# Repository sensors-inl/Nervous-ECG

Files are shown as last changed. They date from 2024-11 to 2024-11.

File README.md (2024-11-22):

<p align="center">
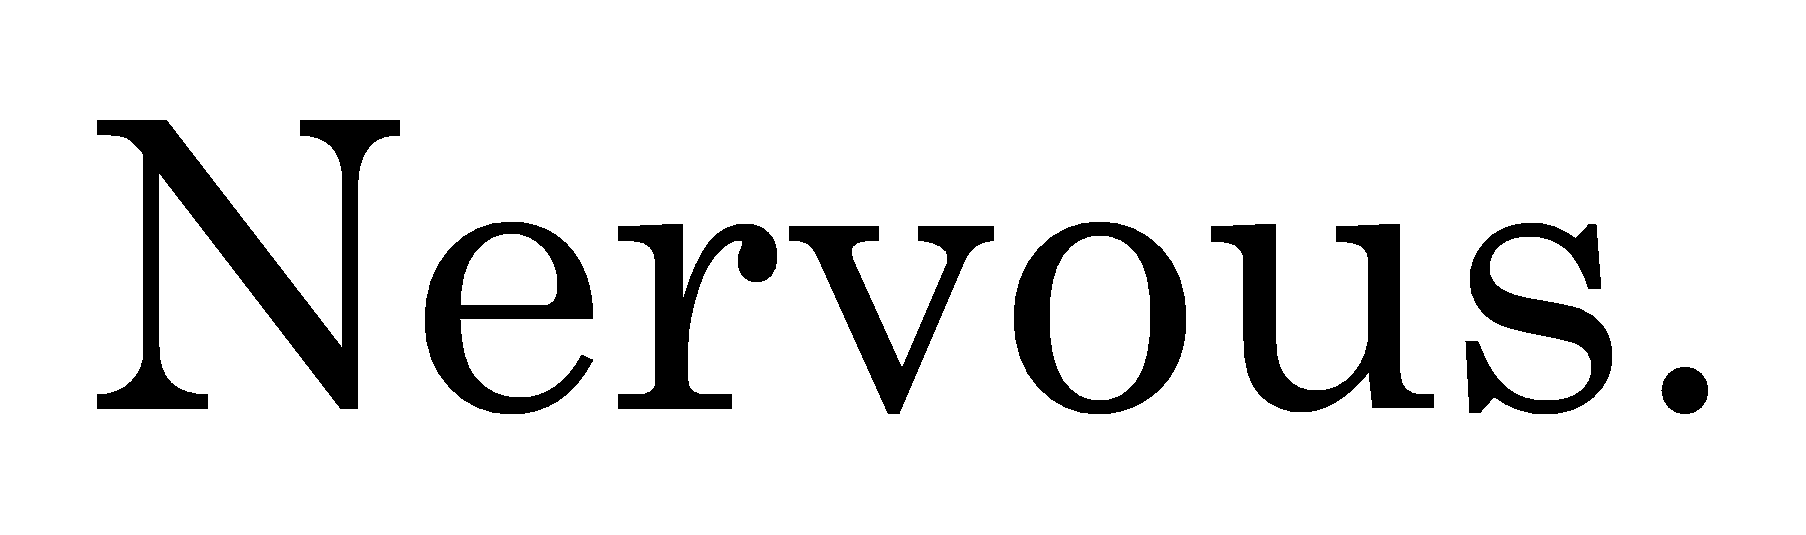
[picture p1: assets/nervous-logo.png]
    
</p>
<p align="center">
    <h1 align="center">Nervous ECG Sensor</h1>
</p>

<p align="center">
    
    
	
	
</p>

## Table of Contents

- [Table of Contents](#table-of-contents)
- [Overview](#overview)
- [Features](#features)
- [Instructions](#instructions)
- [Releases](#releases)
- [Contributing](#contributing)
- [Contact](#contact)
- [License](#license)
- [Acknowledgments](#acknowledgments)

---

## Overview

The **Nervous** project is an initiative based on open-hardware and open-source principles, aimed at providing wearable sensors and software for analyzing the Autonomic Nervous System (ANS) activity.

The **Nervous ECG** project is part of the **[Nervous Toolkit](https://github.com/sensors-inl/Nervous-Toolkit)** and includes hardware design files and firmware source files for creating an electrocardiogram (ECG) sensor to measure the ECG signal **from the hands or forearms**.
The device is wireless and transmits the collected data via Bluetooth Low Energy.

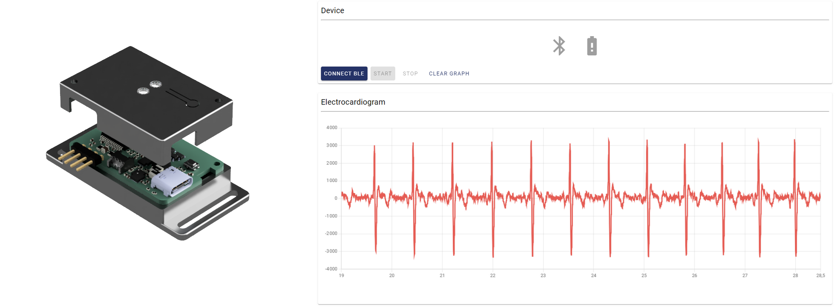
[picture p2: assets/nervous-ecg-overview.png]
Illustration of the Nervous ECG sensor and real-time data shown on the application Nervous ECG sensor and application


---

## Features

This project is actually a collection of three sub-projects for the sensor design, located in the following directories:

[hardware](./hardware/): This folder contains ECAD files for producing PCBs and assembling circuits for a wireless wrist-worn ECG sensor.
A archive (.zip) containing the design and manufacturing/assembly files for the sensor is available in the releases of this project.

[firmware](./firmware/): This folder contains source files to build binaries for programming the microcontroller.
Precompiled binaries are also provided in the releases of this project.

[web-app](./web-app/): While the sensor is primarily designed to work with the [```nervous-sensors```](https://github.com/sensors-inl/Nervous-Sensors) Python package included in the Nervous Toolkit, a standalone web application is provided for simplified use of the sensor.
It offers sensor control, real-time data visualization, and recording features.
Pre-built executables for both Microsoft Windows and Linux are also available in the releases of this project.

---

## Instructions

Detailed instructions are provided in each subdirectory for manufacturing, programming, and using the sensor.

---

## Releases

Each [release](https://github.com/sensors-inl/Nervous-ECG/releases/latest) contains built firmware and application binaries as well as an archive of ECAD files.

---

## Contributing

Contributions are what make the open-source community such a great place to learn, inspire, and create. Any contributions you make are greatly appreciated. You can open an issue to report a bug, request a feature, or submit a pull request.

---

## Contact

Bertrand MASSOT - [bertrand.massot@insa-lyon.fr](mailto:bertrand.massot@insa-lyon.fr)

---

## License

This project, along with the entire Nervous initiative, is licensed under the [MIT License](https://opensource.org/licenses/MIT). For more details, see the [License](LICENSE.md) file.

---

## Acknowledgments

The main contributors to this project are Bertrand Massot, Matthieu Mesnage, Tristan Habemont and Hugo Buy from INSA Lyon, CNRS, INL UMR 5270, Villeurbanne, France.

This work was supported by the **French National Research Agency (ANR)** under grant **ANR-22-CE31-0023-03 RENFORCE**.

---

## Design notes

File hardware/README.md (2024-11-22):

<p align="center">
    <h1 align="center">Nervous ECG Hardware</h1>
</p>

<p align="center">
    <a href="https://www.kicad.org/">
        
    </a>
    <a href="https://opensource.org/licenses/MIT">
        
    </a>
</p>

## Table of Contents

- [Table of Contents](#table-of-contents)
- [Overview](#overview)
- [Hardware features](#hardware-features)
- [Manufacturing and assembling](#manufacturing-and-assembling)
  - [PCB properties for manufacturing](#pcb-properties-for-manufacturing)
- [Modification](#modification)
- [Casing](#casing)
- [Note on cables and electrodes placement to reduce signal noise](#note-on-cables-and-electrodes-placement-to-reduce-signal-noise)
- [Release](#release)
- [Contributing](#contributing)
- [Contact](#contact)
- [License](#license)
- [Acknowledgments](#acknowledgments)

---

## Overview

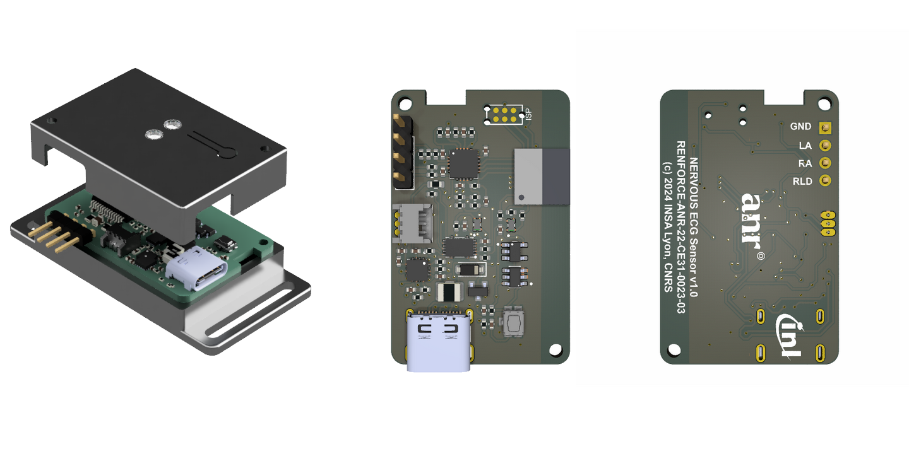
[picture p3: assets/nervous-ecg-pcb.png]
Nervous ECG printed circuit board


This folder contains ECAD files for the production of PCBs and assembly of circuits for the Nervous ECG sensor.
The printed circuit board was designed using the open source electronics design automation suite [KiCad EDA](https://www.kicad.org/) v7.0.8

Originally designed for measuring heart rate via electrodes placed on the forearms or hands, this sensor utilizes the AD8232 along with passive components, as described in the "EXERCISE APPLICATION: HEART RATE MEASURED AT THE HANDS" section on page 27 of the [datasheet](<https://www.analog.com/media/en/technical-documentation/data-sheets/ad8232.pdf>).
You can modify this configuration for different applications and electrode placements.

The microcontroller used is the nRF52840 (Nordic Semiconductor) within the ISP1807 System-in-Package (Insight SiP).

---

## Hardware features

- USB-C connector for charging the battery
- Embedded LiPo battery charger and I2C fuel gauge
- On/Off SPST button (enables/disables the voltage regulator)
- RGB status LED
- AD8232 ECG AFE with a 7 Hz - 24 Hz bandpass filter (56 dB @ 13 Hz) and RLD
- nRF52840 (ISP1807) with Bluetooth Low Energy

---

## Manufacturing and assembling

The following files are available in the `Export` folder:

- **Export/Manufacturing**: contains Gerber (.gbr) and drill files (.drl)
- **Export/Assembly**: contains assembly drawing (.pdf), pick and place files (.pos), and BOM (.csv)

---

### PCB properties for manufacturing

Some PCB manufacturers may require the following properties. The table below summarizes the principal PCB properties:

| Property                    | Value              |
| --------------------------- | ------------------ |
| Dimensions                  | 21.5 mm x 33.5 mm  |
| Number of layers            | 2                  |
| Minimal insulation width    | 0.150 mm           |
| Minimal trace width         | 0.150 mm           |
| Minimal hole size           | 0.200 mm           |

---

## Modification

The `Source` folder contains the original KiCad project, created using KiCad version 7.0.8.

---

## Casing

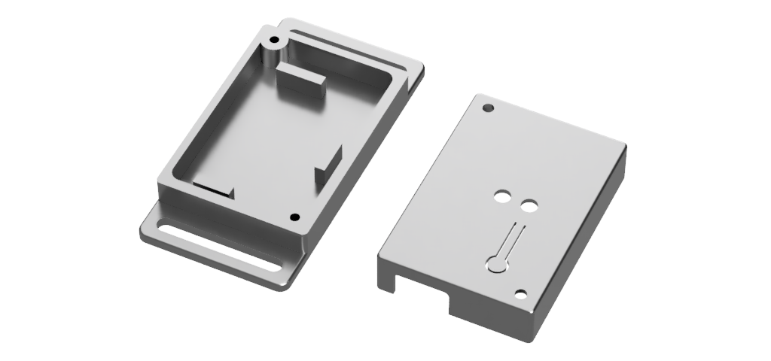
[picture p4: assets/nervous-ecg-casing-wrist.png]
Nervous ECG casing for wrist attachment


Several 3D models are available for producing a casing for the electronics. STEP and STL files are located in the `Casing` folder:

- **casing_top** and **casing_bottom** are two parts that assemble together with two M2 screws, where the PCB and a 150 mAh LiPo battery fit. A specially designed battery compartment ensures that it does not overlap with the antenna of the ISAP1807 chip located on the longitudinal edge of the PCB. The design of the bottom part includes handles for wrist attachment.
- **casing_bottom_controller** is a modified version of the bottom part, designed to mount the electronics circuit and battery onto a Valve Index controller for ECG assessment during virtual environment sessions.

---

## Note on cables and electrodes placement to reduce signal noise

This sensor is designed to capture ECG signals under various conditions while minimizing discomfort. To achieve this, it uses high gain to support electrode placement on the hands or forearms, where signal strength is typically lower. However, this placement also amplifies sensitivity to motion artifacts, which can affect heart rate accuracy.

To minimize these artifacts, we recommend using solid gel electrodes, such as the 3M 2650. The sensor features a simple 2.54 mm, 3-way header for custom electrode connections. It is recommended to use short cables for the two electrodes near the device (RLD and RA), and a longer cable for the third electrode on the opposite arm (LA). The cables are designed with female crimp terminals at the sensor end and snap adapters at the electrode end. We recommend using cables with low triboelectric effect, such as Belden 9239 Low Noise Coaxial cable. To reduce noise from connector friction, securely hold the electrodes and cables near the electrodes with medical tape.

---

## Release

The entire folder is provided as an archive (`Nervous-ECG-hardware-vX.X.X.zip`) in the [releases](https://github.com/sensors-inl/Nervous-ECG/releases/latest) of this project.

---

## Contributing

Contributions are what make the open-source community great. Any contributions are greatly appreciated. You can open an issue to report a bug, request a feature, or submit a pull request.

---

## Contact

**Bertrand MASSOT**  
[bertrand.massot@insa-lyon.fr](mailto:bertrand.massot@insa-lyon.fr)

---

## License

This project, along with the entire Nervous initiative, is licensed under the [MIT License](https://opensource.org/licenses/MIT). For more details, see the [License](LICENSE.md) file.

---

## Acknowledgments

The main contributors to this project are  Bertrand Massot, Matthieu Mesnage, and Hugo Buy from INSA Lyon, CNRS, INL UMR 5270, Villeurbanne, France.

This work was supported by the **French National Research Agency (ANR)** under grant **ANR-22-CE31-0023-03 RENFORCE**.

---

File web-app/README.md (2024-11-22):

<p align="center">
    <h1  align="center">Nervous ECG Application</h1>
</p>

<p align="center">
    
    
    <a href="https://opensource.org/licenses/MIT">
        
    </a>
</p>

## Table of Contents

- [Table of Contents](#table-of-contents)
- [Overview](#overview)
- [Usage](#usage)
- [Building Executable Binaries for Windows and Linux](#building-executable-binaries-for-windows-and-linux)
  - [Prerequisites](#prerequisites)
  - [Build Instructions](#build-instructions)
- [Release](#release)
- [Contributing](#contributing)
- [Contact](#contact)
- [License](#license)
- [Acknowledgments](#acknowledgments)

---

## Overview

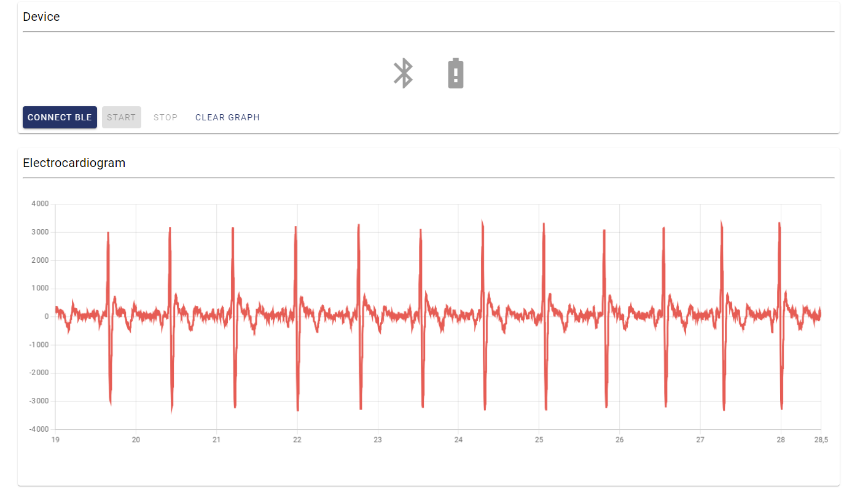
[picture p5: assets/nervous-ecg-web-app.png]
Web application of the Nervous ECG sensor


This repository contains an HTML/JavaScript application that connects to Nervous ECG sensors. The application plots ECG data in real-time and saves the signal to a `.csv` file. It consists of a single static HTML page, `index.html`, along with two JavaScript files: `app.js` (the main application script) and `proto.js` (the JavaScript compilation of the Protocol Buffer files).

This application uses several libraries. For offline usage, local copies of these libraries are included. The following versions of the libraries are currently used:

- [**Chart.js**](https://www.chartjs.org/) (v4.4.0)
- [**google-protobuf**](https://www.npmjs.com/package/google-protobuf) (v3.19.0)
- [**material-components-web**](https://www.npmjs.com/package/material-components-web) (v14.0.0)
- [**cobs**](https://www.npmjs.com/package/cobs) (v0.2.1)

Additional configuration files, such as `forge.config.js`, `jsconfig.json`, `main.js`, and `package.js`, are provided to facilitate building the application into an executable using [**Electron**](https://www.electronjs.org/) and [**Electron Forge**](https://www.electronforge.io/). This allows you to build executables for Windows and Linux by following the instructions below.

---

## Usage

To use the application, simply open `index.html` in a Chromium-based web browser (e.g., Chrome, Microsoft Edge). 

1. Press the **CONNECT** button to scan for available ECG sensors.
2. Once connected, press the **START** button to begin collecting and plotting data in real-time.
3. Press the **STOP** button to stop the data collection and save the data to a `.csv` file.

Since the application runs in the web browser, the `.csv` file will be automatically downloaded, but the entire application runs locally in the browser.

> **Note:** When using the built executable (see below), the application will automatically connect to the first available sensor rather than displaying a list of available sensors.

---

## Building Executable Binaries for Windows and Linux

This application can be built into executables for Windows and Linux using Electron.

### Prerequisites

Before building the application, the following dependencies must be installed:

- [Node.js and npm](https://docs.npmjs.com/downloading-and-installing-node-js-and-npm) (required to install and use Electron and Electron Forge)
- Install Electron: `npm install --save-dev electron`
- Install Electron Forge: `npm install --save-dev @electron-forge/cli`

### Build Instructions

1. Prepare the build environment:

    ```console
    npx electron-forge import
    ```

2. Package the build, specifying the architecture and OS. For example, for Windows, use:

    ```console
    npx electron-forge package --arch=x64 --platform=win32
    ```

    For Linux, use:

    ```console
    npx electron-forge package --arch=x64 --platform=linux
    ```

3. The packaged binaries will be located in the `out/` directory.

---

## Release

Executable binaries for Windows and Linux are automatically built in CI and are available for download as `.zip` archives from each [release](https://github.com/sensors-inl/Nervous-ECG/releases/latest).

---

## Contributing

Contributions are what make the open-source community a great place to learn, inspire, and create. Any contributions you make are greatly appreciated. You can open an issue to report a bug, request a feature, or submit a pull request.

---

## Contact

**Bertrand MASSOT**  
Email: [bertrand.massot@insa-lyon.fr](mailto:bertrand.massot@insa-lyon.fr)

---

## License

This project, as part of the Nervous initiative, is licensed under the [MIT License](https://opensource.org/licenses/MIT). For more details, refer to the [LICENSE](LICENSE.md) file.

---

## Acknowledgments

The primary contributor to this project is **Bertrand Massot** from INSA Lyon, CNRS, INL UMR 5270, Villeurbanne, France.

This work was supported by the **French National Research Agency (ANR)** under grant **ANR-22-CE31-0023-03 RENFORCE**.

---

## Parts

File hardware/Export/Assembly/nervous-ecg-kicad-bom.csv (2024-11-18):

Id | Quantity | Designator | Description | Manufacturer | Manufacturer Part Number | Supplier | Supplier Part Number
1 | 1 | BT1 | BATT LI-PO 3.7V 165MAH | BAK TECHNOLOGY | LP-402025-1S-3 | FARNELL | 2077885
2 | 5 | C1, C2, C6, C8, C9 | CAP CER 1UF 10V X5R 0402 | Yageo | CC0402KRX5R6BB105 | Farnell | 1458896
3 | 2 | C3, C4 | CAP CER 4.7UF 6.3V X5R 0402 | Yageo | CC0402KRX5R5BB475 | Farnell | 3369135
4 | 1 | C5 | CAP CER 0.47UF 10V X5R 0402 | Yageo | CC0402KRX5R6BB474 | Farnell | 3369138
5 | 3 | C7, C11, C13 | CAP CER 0.1UF 16V X7R 0402 | Yageo | CC0402JRX7R7BB104 | Farnell | 3369125
6 | 1 | C10 | CAP CER 1000PF 50V X7R 0402 | Yageo | CC0402KRX7R9BB102 | Farnell | 3019380
7 | 2 | C12, C14 | CAP CER 0.22UF 10V X5R 0402 | Yageo | CC0402KRX5R6BB224 | Farnell | 9402055
8 | 1 | C15 | CAP CER 22000PF 16V X7R 0402 | Yageo | CC0402KRX7R7BB223 | Farnell | 3019299
9 | 1 | C16 | CAP CER 3300PF 50V X7R 0402 | Yageo | CC0402KRX7R9BB332 | Farnell | 3873402
10 | 1 | D1 | DIODE SCHOTTKY 20V 500MA SOD123 | STMicroelectronics | STPS0520Z | FARNELL | 1467545
11 | 2 | D4, D5 | LED RGB CLEAR 4SMD | KINGBRIGHT | APHF1608LSEEQBDZGKC | DIGIKEY | 754-2143-1-ND
12 | 1 | F1 | PTC RESET FUSE 16V 500MA 1210 | BEL | 0ZCH0050FF2G | Farnell | 2848519
13 | 1 | J1 | CONN RCP USB3.1 TYPEC 24P SMD RA | MOLEX | 105450-0101 | FARNELL | 2524076
14 | 1 | J2 | MOLEX 53048-0310 | MOLEX | 53048-0310 | FARNELL | 9732918
15 | 1 | J4 | CONN HEADER R/A 4POS 2.54MM | AMPHENOL COMMUNICATIONS SOLUTIONS | 77315-118-04LF | FARNELL | 3728851
16 | 1 | R1 | RES SMD 3K OHM 1% 1/16W 0402 | Yageo | AC0402FR-073KL | Farnell | 3951323
17 | 1 | R3 | RES 5.9K OHM 1% 1/16W 0402 | Yageo | RC0402FR-075K9L | Farnell | 3951010
18 | 6 | R5, R6, R7, R8, R10, R14 | RES 10K OHM 1% 1/16W 0402 | Yageo | RC0402FR-0710KL | Farnell | 9239359
19 | 1 | R9 | RES 0.01 OHM 1% 1/10W 0603 | Yageo | RL0603FR-070R01L | Farnell | 8067767
20 | 5 | R11, R12, R13, R18, R19 | RES SMD 10M OHM 1% 1/16W 0402 | Yageo | RC0402FR-0710ML | Farnell | 1458733
21 | 2 | R15, R16 | RES SMD 180K OHM 1% 1/10W 0402 | Panasonic | ERJ-H2RF1803X | Farnell | 3644222
22 | 1 | R17 | RES SMD 360K OHM 1% 1/16W 0402 | Yageo | RC0402FR-07360KL | Digi-Key | 311-360KLRCT-ND
23 | 3 | R20, R21, R27 | RES SMD 1M OHM 1% 1/16W 0402 | Yageo | RC0402FR-071ML | Farnell | 9239588
24 | 3 | R22, R24, R30 | RES 1K OHM 1% 1/16W 0402 | Yageo | RC0402FR-071KL | Farnell | 9239235
25 | 2 | R23, R25 | RES 100K OHM 1% 1/16W 0402 | Yageo | RC0402FR-07100KL | Farnell | 9239472
26 | 2 | R26, R32 | RES 4.7K OHM 1% 1/16W 0402 | Yageo | RC0402FR-074K7L | Farnell | 9239316
27 | 1 | R28 | RES 5.1K OHM 0.5% 1/10W 0402 | PANASONIC | ERJ-U2RD5101X | FARNELL | 3516311
28 | 1 | R29 | RES 5.1K OHM 0.5% 1/10W 0402 | PANASONIC | ERJ-U2RD5101X | FARNELL | 3516311
29 | 1 | U1 | RF TXRX MODULE BT TRACE ANT SMD | INSIGHT SIP | ISP1807-LR-RS | DIGIKEY | 1786-1019-1-ND
30 | 1 | U2 | IC BATT CHG LI-ION 1CELL 16QFN | TEXAS INSTRUMENTS | BQ24074RGTT | FARNELL | 3123775
31 | 1 | U3 | IC BATT FUEL GAUGE LICOO2 12SON | TEXAS INSTRUMENTS | BQ27441DRZR-G1A | FARNELL | 3123775
32 | 1 | U4 | IC REG LINEAR 3.3V 200MA SOT23-5 | TEXAS INSTRUMENTS | TPS7A0533PDBVR | DIGIKEY | 296-TPS7A0533PDBVRDKR-ND
33 | 1 | U5 | IC ECG FRONT END 20LFCSP | Analog Devices | AD8232ACPZ-R7 | Farnell | 4029748
34 | 1 | U6 | IC INTFACE SPECIALIZED TSOT23-6 | ANALOG DEVICES | MAX16054AZT+T | FARNELL | 2515822
35 | 1 | U7 | SWITCH TACTILE SPST-NO 0.02A 15V | PANASONIC | EVP-AA502W | FARNELL | 2831733
36 | 1 | U9 | TVS Diode WE-TVS-Standard, VRWM=5.0V | SEMTECH | SM05.TCT | Farnell | 1456392
37 | 1 | U10 | LIGHTPIPE PNL MT CONVEX 0.250" | DIALIGHT | 515-1302-0250F | FARNELL | 3775816

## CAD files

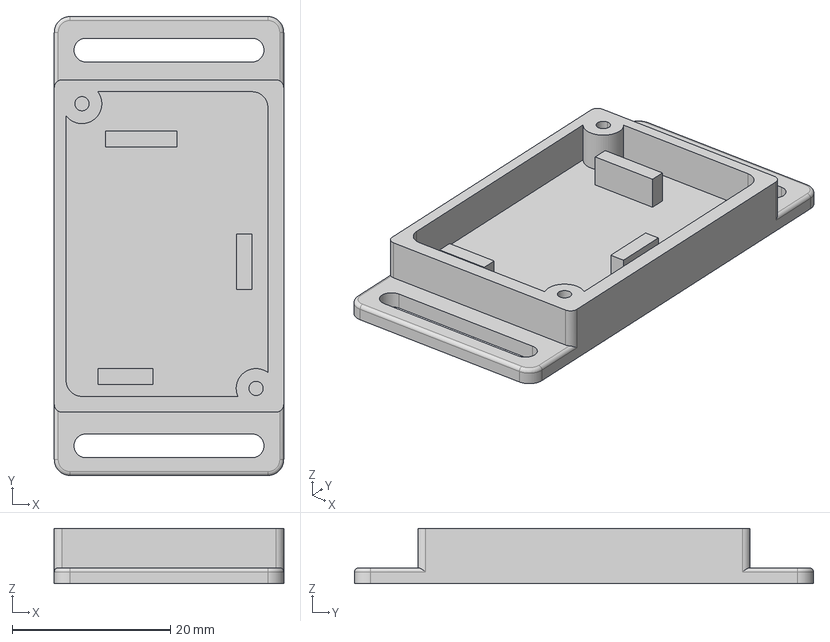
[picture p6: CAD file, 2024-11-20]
hardware/Casing/casing_bottom.step
29.0 x 58.0 x 7.00 mm

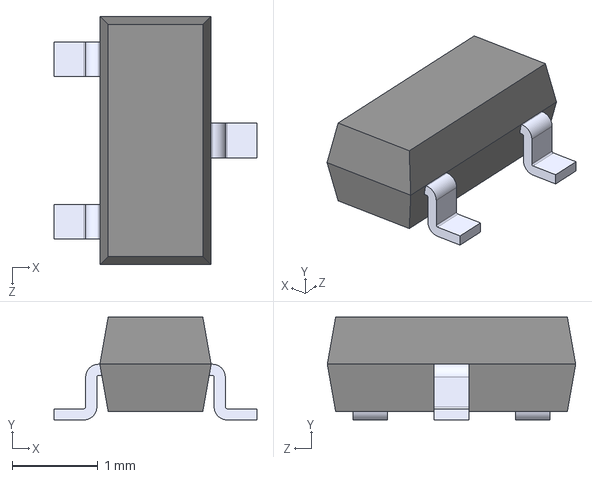
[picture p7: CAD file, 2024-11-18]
hardware/Source/nervous-ecg-3dmodels/SM05.TCT.STEP
2.37 x 1.20 x 2.90 mm

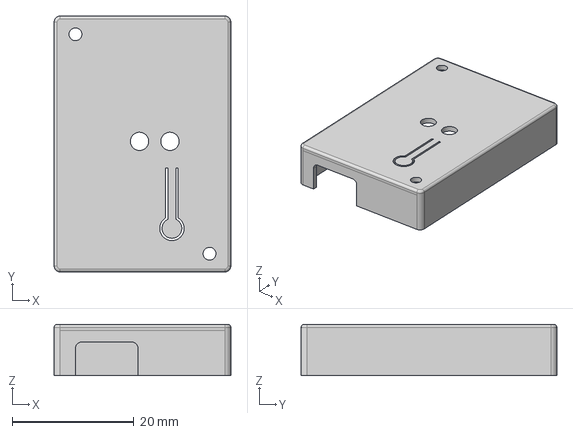
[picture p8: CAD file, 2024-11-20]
hardware/Casing/casing_top.step
29.0 x 42.0 x 8.40 mm

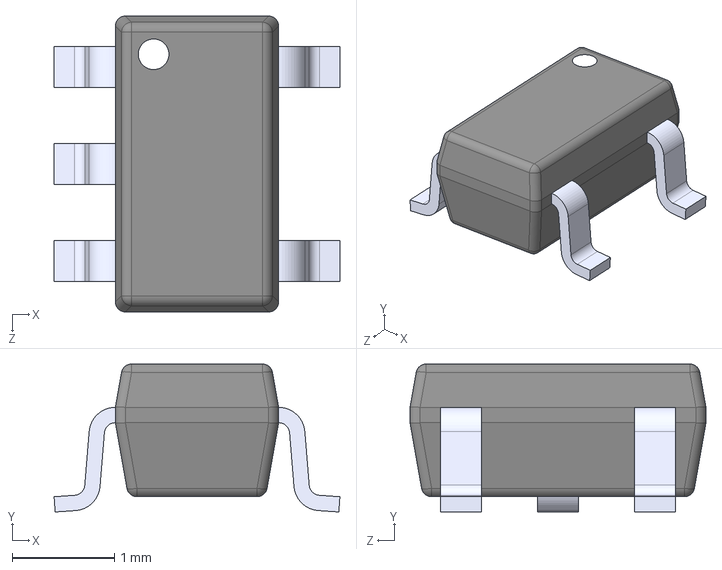
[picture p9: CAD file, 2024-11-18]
hardware/Source/nervous-ecg-3dmodels/TPS7A0533PDBVR.step
2.80 x 1.45 x 2.90 mm

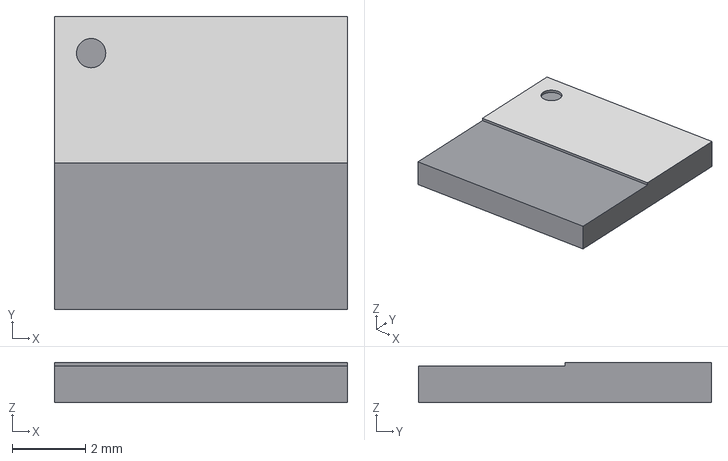
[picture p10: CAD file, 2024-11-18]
hardware/Source/nervous-ecg-3dmodels/ISP1807-LR.step
8.00 x 8.00 x 1.10 mm

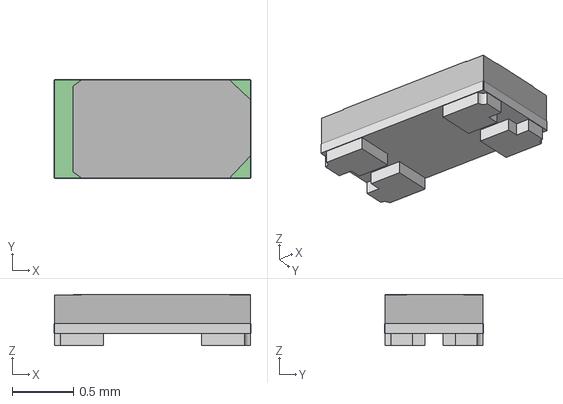
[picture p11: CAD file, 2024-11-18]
hardware/Source/nervous-ecg-3dmodels/LED_RGB_SMD_0603.step
1.61 x 0.81 x 0.42 mm

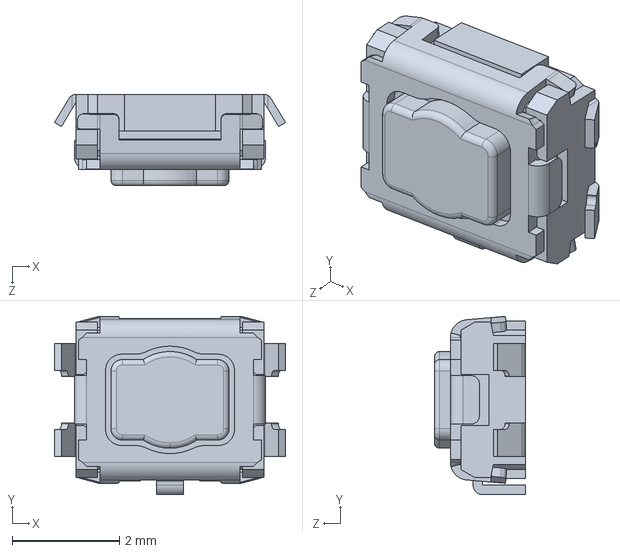
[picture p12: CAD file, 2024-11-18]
hardware/Source/nervous-ecg-3dmodels/EVPAA-102K_302K_502W_702W_902Q.STEP
4.30 x 3.32 x 1.70 mm

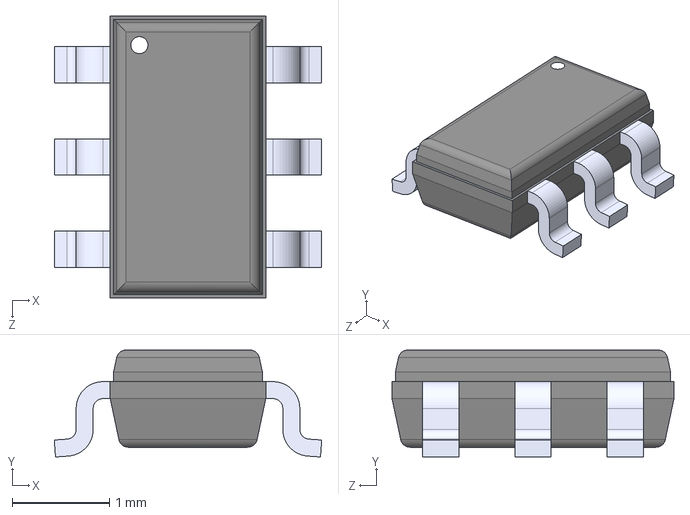
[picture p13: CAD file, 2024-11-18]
hardware/Source/nervous-ecg-3dmodels/MAX16054AZT+T.STEP
2.75 x 1.10 x 2.90 mm

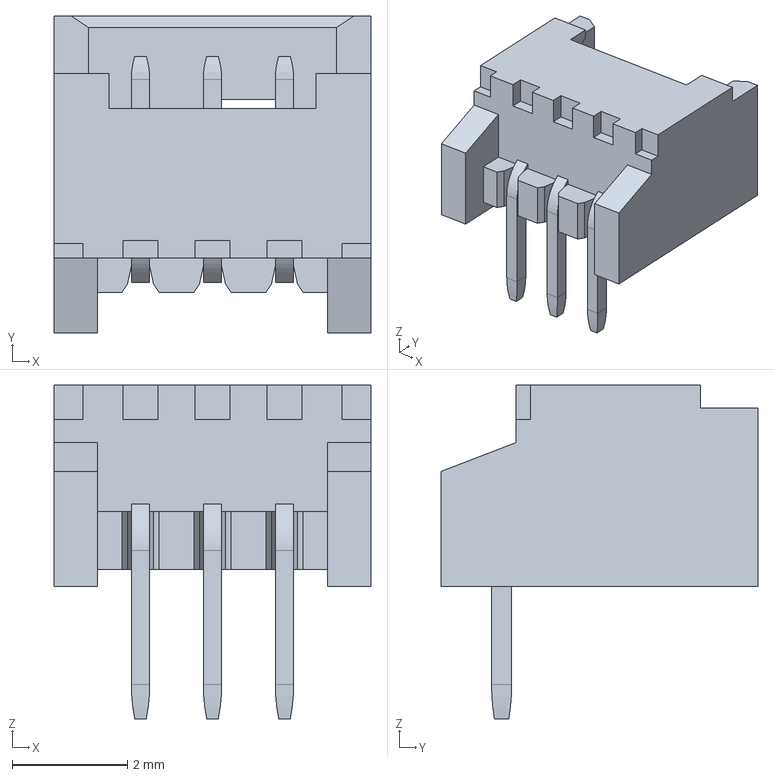
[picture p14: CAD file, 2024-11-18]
hardware/Source/nervous-ecg-3dmodels/530480310.stp
5.50 x 5.50 x 5.80 mm

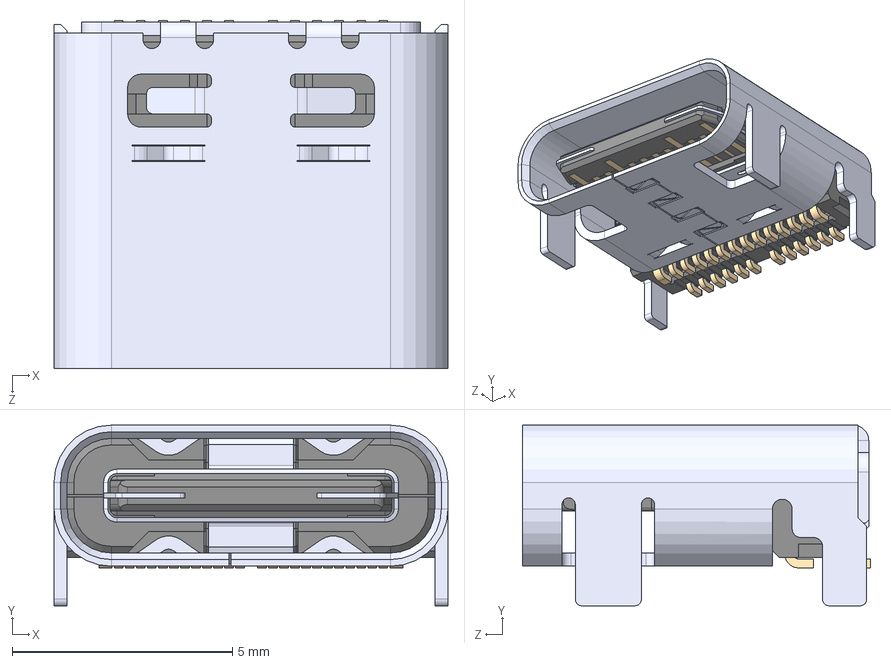
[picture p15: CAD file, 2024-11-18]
hardware/Source/nervous-ecg-3dmodels/105450-0101.step
8.94 x 4.10 x 7.90 mm

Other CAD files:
hardware/Casing/casing_bottom.stl
hardware/Casing/casing_top.stl

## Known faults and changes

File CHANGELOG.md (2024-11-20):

# Changelog

## [1.0.0] - 2024-11-18

🎉 _First release !_

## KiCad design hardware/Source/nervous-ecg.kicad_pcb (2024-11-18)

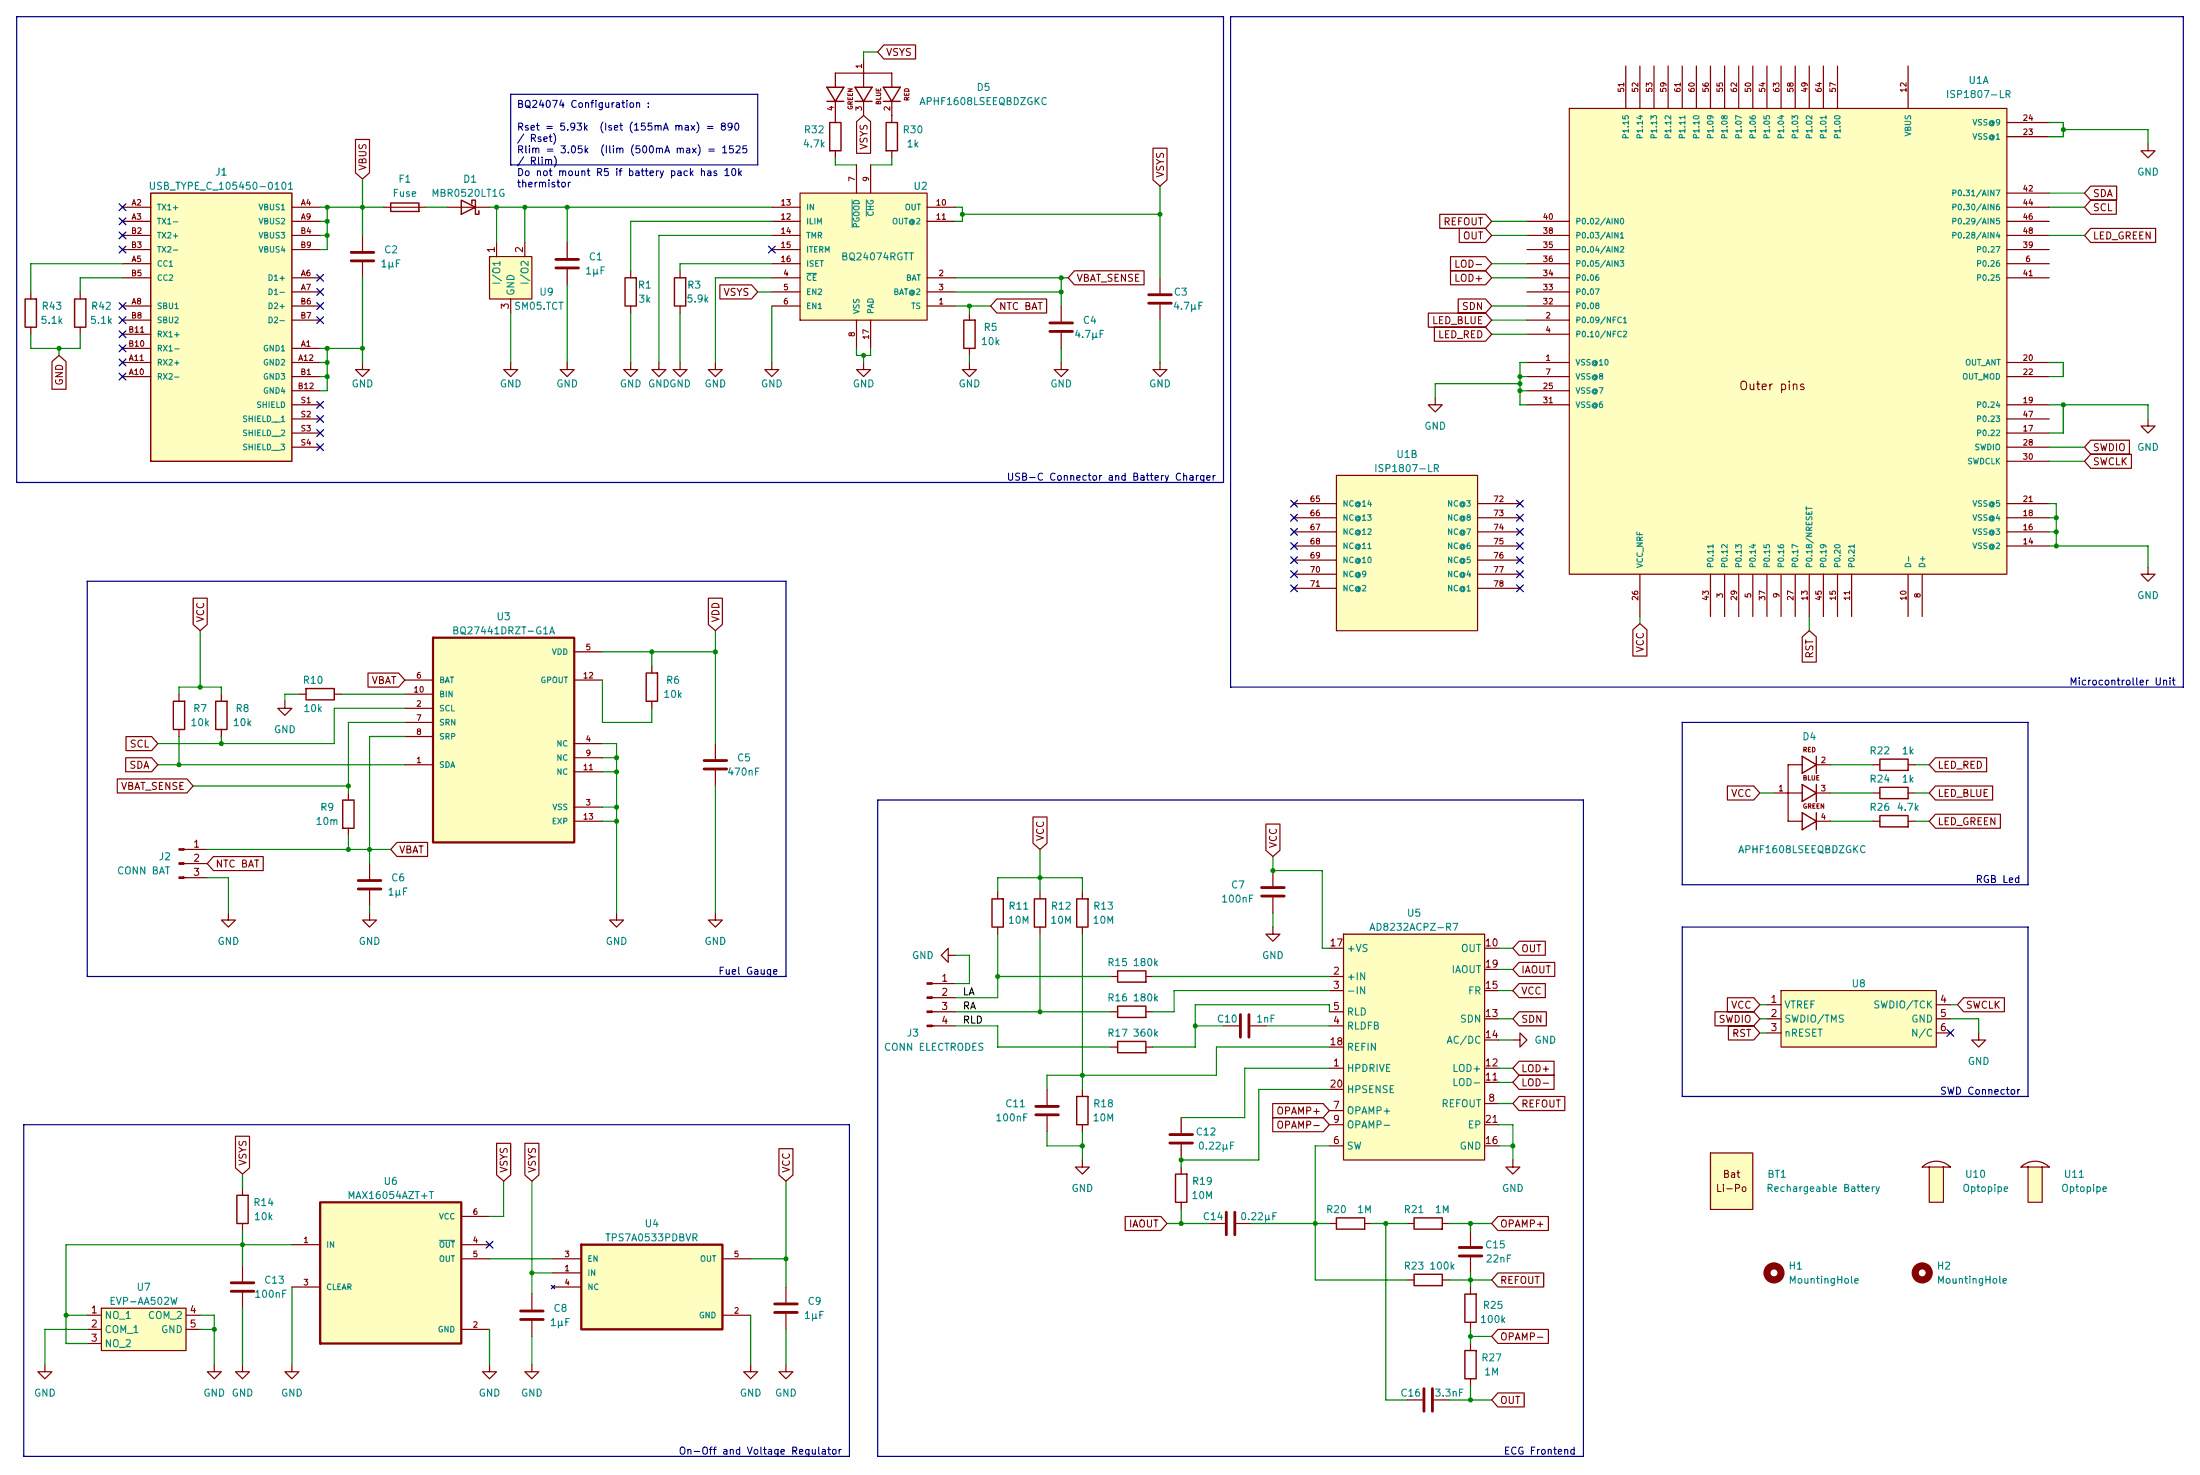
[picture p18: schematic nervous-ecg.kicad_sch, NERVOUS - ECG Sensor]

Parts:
BT1: BATT LI-PO 3.7V 165MAH; Manufacturer Part Number LP-402025-1S-3
C1, C2, C6, C8, C9: CAP CER 1UF 10V X5R 0402; C_0402_1005Metric; Manufacturer Part Number CC0402KRX5R6BB105
C3, C4: CAP CER 4.7UF 6.3V X5R 0402; C_0402_1005Metric; Manufacturer Part Number CC0402KRX5R5BB475
C5: CAP CER 0.47UF 10V X5R 0402; C_0402_1005Metric; Manufacturer Part Number CC0402KRX5R6BB474
C7, C11, C13: CAP CER 0.1UF 16V X7R 0402; C_0402_1005Metric; Manufacturer Part Number CC0402JRX7R7BB104
C10: CAP CER 1000PF 50V X7R 0402; C_0402_1005Metric; Manufacturer Part Number CC0402KRX7R9BB102
C12, C14: CAP CER 0.22UF 10V X5R 0402; C_0402_1005Metric; Manufacturer Part Number CC0402KRX5R6BB224
C15: CAP CER 22000PF 16V X7R 0402; C_0402_1005Metric; Manufacturer Part Number CC0402KRX7R7BB223
C16: CAP CER 3300PF 50V X7R 0402; C_0402_1005Metric; Manufacturer Part Number CC0402KRX7R9BB332
D1: DIODE SCHOTTKY 20V 500MA SOD123; D_SOD-123; Manufacturer Part Number STPS0520Z
D4, D5: LED RGB CLEAR 4SMD; APHF1608LSEEQBDZGKC; Manufacturer Part Number APHF1608LSEEQBDZGKC
F1: PTC RESET FUSE 16V 500MA 1210; Fuse_1210_3225Metric; Manufacturer Part Number 0ZCH0050FF2G
H1, H2: MountingHole; MountingHole_2mm
J1: CONN RCP USB3.1 TYPEC 24P SMD RA; USB_TYPE_C_105450-0101; Manufacturer Part Number 105450-0101
J2: MOLEX 53048-0310; CONN_BAT_53048-0310; Manufacturer Part Number 53048-0310
J3: CONN HEADER R/A 4POS 2.54MM; CONN_ELECTRODE; Manufacturer Part Number 77315-118-04LF
R1: RES SMD 3K OHM 1% 1/16W 0402; R_0402_1005Metric; Manufacturer Part Number AC0402FR-073KL
R3: RES 5.9K OHM 1% 1/16W 0402; R_0402_1005Metric; Manufacturer Part Number RC0402FR-075K9L
R5, R6, R7, R8, R10, R14: RES 10K OHM 1% 1/16W 0402; R_0402_1005Metric; Manufacturer Part Number RC0402FR-0710KL
R9: RES 0.01 OHM 1% 1/10W 0603; R_0603_1608Metric; Manufacturer Part Number RL0603FR-070R01L
R11, R12, R13, R18, R19: RES SMD 10M OHM 1% 1/16W 0402; R_0402_1005Metric; Manufacturer Part Number RC0402FR-0710ML
R15, R16: RES SMD 180K OHM 1% 1/10W 0402; R_0402_1005Metric; Manufacturer Part Number ERJ-H2RF1803X
R17: RES SMD 360K OHM 1% 1/16W 0402; R_0402_1005Metric; Manufacturer Part Number RC0402FR-07360KL
R20, R21, R27: RES SMD 1M OHM 1% 1/16W 0402; R_0402_1005Metric; Manufacturer Part Number RC0402FR-071ML
R22, R24, R30: RES 1K OHM 1% 1/16W 0402; R_0402_1005Metric; Manufacturer Part Number RC0402FR-071KL
R23, R25: RES 100K OHM 1% 1/16W 0402; R_0402_1005Metric; Manufacturer Part Number RC0402FR-07100KL
R26, R32: RES 4.7K OHM 1% 1/16W 0402; R_0402_1005Metric; Manufacturer Part Number RC0402FR-074K7L
R42: RES 5.1K OHM 0.5% 1/10W 0402; C_0402_1005Metric; Manufacturer Part Number ERJ-U2RD5101X
R43: RES 5.1K OHM 0.5% 1/10W 0402; R_0402_1005Metric; Manufacturer Part Number ERJ-U2RD5101X
U1: RF TXRX MODULE BT TRACE ANT SMD; ISP1807-LR; Manufacturer Part Number ISP1807-LR-RS
U2: IC BATT CHG LI-ION 1CELL 16QFN; BQ24074RGTx; Manufacturer Part Number BQ24074RGTT
U3: IC BATT FUEL GAUGE LICOO2 12SON; BQ27441DRZR-G1A; Manufacturer Part Number BQ27441DRZR-G1A
U4: IC REG LINEAR 3.3V 200MA SOT23-5; TPS7A0533PDBVR; Manufacturer Part Number TPS7A0533PDBVR
U5: IC ECG FRONT END 20LFCSP; AD8232ACPZ-R7; Manufacturer Part Number AD8232ACPZ-R7
U6: IC INTFACE SPECIALIZED TSOT23-6; MAX16054AZT+T; Manufacturer Part Number MAX16054AZT+T
U7: SWITCH TACTILE SPST-NO 0.02A 15V; EVP-AA502W; Manufacturer Part Number EVP-AA502W
U8: TC2030-MCP-NL
U9: TVS Diode WE-TVS-Standard, VRWM=5.0V; SM05.TCT; Manufacturer Part Number SM05.TCT
U10, U11: LIGHTPIPE PNL MT CONVEX 0.250"; Manufacturer Part Number 515-1302-0250F

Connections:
/LA: J3.2, R11.1, R15.1
/RA: J3.3, R12.1, R16.1
/RLD: J3.4, R17.1
GND: C1.2, C2.2, C3.1, C4.2, C5.2, C6.2, C7.2, C8.2, C9.2, C11.2, C13.2, J1.A1 (GND1), J1.A12 (GND2), J1.B1 (GND3), J1.B12 (GND4), J2.3, J3.1, R1.1, R3.1, R5.1, R10.2, R18.1, U1.1 (VSS@10), U1.7 (VSS@8), U1.14 (VSS@2), U1.16 (VSS@3), U1.17 (P0.22), U1.18 (VSS@4), U1.19 (P0.24), U1.21 (VSS@5), U1.23 (VSS@1), U1.24 (VSS@9), U1.25 (VSS@7), U1.31 (VSS@6), U2.4 (~CE), U2.6 (EN1), U2.8 (VSS), U2.14 (TMR), U2.17 (PAD), U3.3 (VSS), U3.4 (NC), U3.9 (NC), U3.11 (NC), U3.13 (EXP), U4.2 (GND), U5.14 (AC/DC), U5.16 (GND), U5.21 (EP), U6.2 (GND), U6.3 (CLEAR), U7.2 (COM_1), U7.4 (COM_2), U7.5 (GND), U8.5 (GND), U9.3 (GND); also elsewhere on the board
IAOUT: C14.2, R19.1, U5.19 (IAOUT)
LED_BLUE: R24.2, U1.2 (P0.09/NFC1)
LED_GREEN: R26.2, U1.48 (P0.28/AIN4)
LED_RED: R22.2, U1.4 (P0.10/NFC2)
LOD+: U1.34 (P0.06), U5.12 (LOD+)
LOD-: U1.36 (P0.05/AIN3), U5.11 (LOD-)
NTC BAT: J2.2, R5.2, U2.1 (TS)
unnamed: C16.2, R20.2, R21.1
unnamed: D1.2 (A), F1.2
unnamed: C1.1, D1.1 (K), U2.13 (IN), U9.1 (I/O1), U9.2 (I/O2)
unnamed: D4.2, R22.1
unnamed: D4.3, R24.1
unnamed: D4.4, R26.1
unnamed: D5.2, R30.1
unnamed: D5.4, R32.1
unnamed 19: J1.A5 (CC1); also elsewhere on the board
unnamed 20: J1.B5 (CC2); also elsewhere on the board
unnamed: U1.20 (OUT_ANT), U1.22 (OUT_MOD)
unnamed: R1.2, U2.12 (ILIM)
unnamed: R3.2, U2.16 (ISET)
unnamed: R30.2, U2.9 (~CHG)
unnamed: R32.2, U2.7 (~PGOOD)
unnamed: R10.1, U3.10 (BIN)
unnamed: R6.1, U3.12 (GPOUT)
unnamed: U4.3 (EN), U6.5 (OUT)
unnamed: R15.2, U5.2 (+IN)
unnamed: R16.2, U5.3 (-IN)
unnamed: C12.1, U5.1 (HPDRIVE)
unnamed: C12.2, R19.2, U5.20 (HPSENSE)
unnamed: C11.1, R13.1, R18.2, U5.18 (REFIN)
unnamed: C10.2, R17.2, U5.5 (RLD)
unnamed: C10.1, U5.4 (RLDFB)
unnamed: C14.1, R20.1, R23.1, U5.6 (SW)
unnamed: C13.1, R14.1, U6.1 (IN), U7.1 (NO_1), U7.3 (NO_2)
OPAMP+: C15.1, R21.2, U5.7 (OPAMP+)
OPAMP-: R25.1, R27.2, U5.9 (OPAMP-)
OUT: C16.1, R27.1, U1.38 (P0.03/AIN1), U5.10 (OUT)
REFOUT: C15.2, R23.2, R25.2, U1.40 (P0.02/AIN0), U5.8 (REFOUT)
RST: U1.13 (P0.18/NRESET), U8.3 (nRESET)
SCL: R8.1, U1.44 (P0.30/AIN6), U3.2 (SCL)
SDA: R7.1, U1.42 (P0.31/AIN7), U3.1 (SDA)
SDN: U1.32 (P0.08), U5.13 (SDN)
SWCLK: U1.30 (SWDCLK), U8.4 (SWDIO/TCK)
SWDIO: U1.28 (SWDIO), U8.2 (SWDIO/TMS)
VBAT: C6.1, J2.1, R9.2, U3.6 (BAT), U3.8 (SRP)
VBAT_SENSE: C4.1, R9.1, U2.2 (BAT), U2.3 (BAT@2), U3.7 (SRN)
VBUS: C2.1, F1.1, J1.A4 (VBUS1), J1.A9 (VBUS2), J1.B4 (VBUS3), J1.B9 (VBUS4)
VCC: C7.1, C9.1, D4.1, R7.2, R8.2, R11.2, R12.2, R13.2, U1.26 (VCC_NRF), U4.5 (OUT), U5.15 (FR), U5.17 (+VS), U8.1 (VTREF)
VDD: C5.1, R6.2, U3.5 (VDD)
VSYS: C3.2, C8.1, D5.1, D5.3, R14.2, U2.5 (EN2), U2.10 (OUT), U2.11 (OUT@2), U4.1 (IN), U6.6 (VCC)

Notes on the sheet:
BQ24074 Configuration : Rset = 5.93k (Iset (155mA max) = 890 / Rset) Rlim = 3.05k (Ilim (500mA max) = 1525 / Rlim) Do not mount R5 if battery pack has 10k thermistor
RGB Led
Fuel Gauge
USB-C Connector and Battery Charger
ECG Frontend
SWD Connector
Microcontroller Unit
On-Off and Voltage Regulator

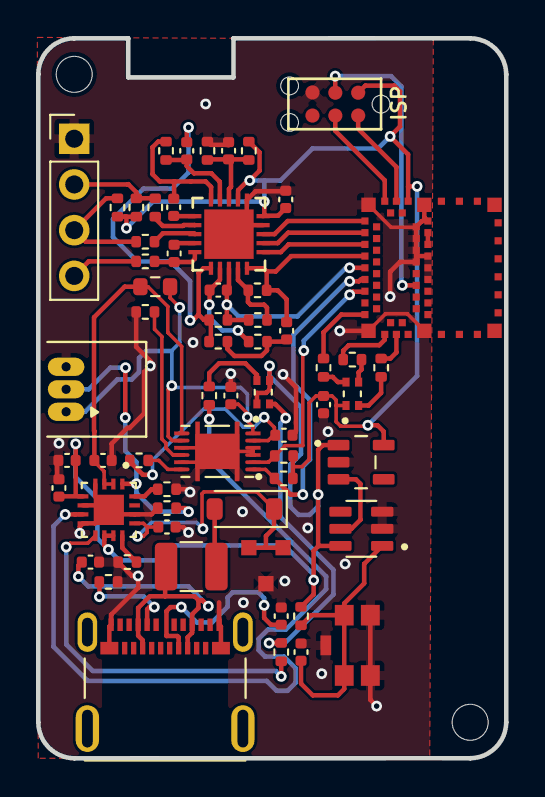
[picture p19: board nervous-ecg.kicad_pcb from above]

Board: 2 copper layers, 26.0 x 40.0 mm, 63 parts (0 on the bottom side), 54 nets.

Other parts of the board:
R28: RES 5.1K OHM 0.5% 1/10W 0402; R_0402_1005Metric
R29: RES 5.1K OHM 0.5% 1/10W 0402; C_0402_1005Metric

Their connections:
GND: R28.1, R29.1; also elsewhere on the board
unnamed 19: R28.2; also elsewhere on the board
unnamed 20: R29.2; also elsewhere on the board

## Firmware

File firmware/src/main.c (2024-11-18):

/**
 *******************************************************************************
 * @file    main.c
 * @author  Bertrand Massot (bertrand.massot@insa-lyon.fr)
 * @date    2022-02-24
 * @brief   RECAMED ECG project main file
 *******************************************************************************
 */

/*******************************************************************************
 * INCLUDES
 ******************************************************************************/

/* C Standard Library includes */
#include <stdio.h>

/* Zephyr Projet includes */
#include <zephyr/kernel.h>
#include <zephyr/logging/log.h>
#include <zephyr/settings/settings.h>
#include <zephyr/drivers/gpio.h>
#include <zephyr/drivers/sensor.h>
#include <zephyr/bluetooth/services/bas.h>
#include <pb_decode.h>

/* Application includes */
#include "bluetooth/bluetooth.h"
#include "calendar/calendar.h"
#include "measurement.h"
#include "nanocobs/cobs.h"

/* Generated headers */
#include "protocol/protocol.pb.h"
#include "app_version.h"

/*******************************************************************************
 * EXTERN VARIABLES
 ******************************************************************************/

/*******************************************************************************
 * PRIVATE MACROS AND DEFINES
 ******************************************************************************/

#define LOG_MODULE_NAME main
LOG_MODULE_REGISTER(LOG_MODULE_NAME);

#define MEASUREMENT_THREAD_PRIORITY	    -1

#define RGB_LED_BLINK_PERIOD            500     // ms
#define RUN_SLEEP_INTERVAL              60000   // ms

/*******************************************************************************
 * PRIVATE TYPEDEFS
 ******************************************************************************/

/* Application states enumeration */
typedef enum
{
    APP_STATE_MEASURING,
    NUM_OF_APP_STATES,
} app_state_t;

/* USB connection state */
typedef enum
{
    USB_STATE_DISCONNECTED,
    USB_STATE_CHARGING,
    USB_STATE_CHARGE_DONE,
    NUM_OF_USB_STATES,
} usb_state_t;

/*******************************************************************************
 * GLOBAL VARIABLES
 ******************************************************************************/

K_THREAD_STACK_DEFINE(measurement_stack_area, 512);
struct k_thread measurement_thread;
k_tid_t measurement_thread_tid;

K_THREAD_STACK_DEFINE(status_stack_area, 512);
struct k_thread status_thread;

/*******************************************************************************
 * STATIC FUNCTION PROTOTYPES
 ******************************************************************************/

/* Measurement thread control function (called async in working queue)*/
static void measurement_start(struct k_work * work);
static void measurement_stop (struct k_work * work);

/* BLE connection events */
static void ble_evt_callback(ble_event_type_t event);
/* BLE NUS data events */
static void ble_rx_callback(const uint8_t *const p_data, uint16_t length);

/* Fuel gauge helper */
static int32_t get_state_of_charge(const struct device *dev);

/* RGB LEd helpers */
static void rgb_led_init(void);
static void rgb_led_set(bool red, bool green, bool blue);
static void rgb_led_blink_blue(void);
static void rgb_led_timer_handler(struct k_timer *timer);

/*******************************************************************************
 * STATIC VARIABLES
 ******************************************************************************/

/* Start and stop work tasks */
K_WORK_DEFINE(start_measure, measurement_start);
K_WORK_DEFINE(stop_measure,  measurement_stop);

/* RGB led timer for blinking */
K_TIMER_DEFINE(rgb_led_timer, rgb_led_timer_handler, NULL);

/* RGB Led pins */
static const struct gpio_dt_spec led_red_pin    = GPIO_DT_SPEC_GET_BY_IDX(DT_PATH(zephyr_user), led_rgb_gpios, 0);
static const struct gpio_dt_spec led_green_pin  = GPIO_DT_SPEC_GET_BY_IDX(DT_PATH(zephyr_user), led_rgb_gpios, 1);
static const struct gpio_dt_spec led_blue_pin   = GPIO_DT_SPEC_GET_BY_IDX(DT_PATH(zephyr_user), led_rgb_gpios, 2);

/* Fuel gauge device */
static const struct device *fuel_gauge = DEVICE_DT_GET(DT_NODELABEL(bq27441));

/* Store global application state */
static app_state_t m_app_state;

/* Message reception buffers */
static uint8_t message[Timestamp_size + 1];
static Timestamp timestamp;

/*******************************************************************************
 * GLOBAL FUNCTIONS
 ******************************************************************************/
int main(void)
{
    printk("\n");
    printk("ECG Firmware version %s\n", APP_VERSION_STRING);

    /* Initialize RGB led pins and set white color to inform about boot */
    rgb_led_init();
    rgb_led_set(true, true, true);

    CAL_Init();

	/* Start Bluetooth stack */
	BLE_Init();
    BLE_SetEventCallback(ble_evt_callback);
    BLE_SetReceiveCallback(ble_rx_callback);

    /* Initialize and set frontend in shutdown */
    MEAS_Init();
    /* Create thread which will be internally paused immediately */
	measurement_thread_tid = k_thread_create(&measurement_thread, measurement_stack_area, 
									K_THREAD_STACK_SIZEOF(measurement_stack_area), 
									MEAS_Thread, NULL, NULL, NULL, 
									MEASUREMENT_THREAD_PRIORITY, 0, K_NO_WAIT);
	k_thread_name_set(measurement_thread_tid, "Measurement");

    /* Start advertising */
	BLE_StartAdvertising();
    rgb_led_blink_blue();

    printk("\n*** Application started ***\n\n");

	for (;;) {

        /* Periodically retrieve battery state */
        int battery = get_state_of_charge(fuel_gauge);
        bt_bas_set_battery_level(battery);  
        if (battery < 20) {
            rgb_led_set(true, false, false);
        }
        
        k_sleep(K_MSEC(RUN_SLEEP_INTERVAL));

	}
	
}


/*******************************************************************************
 * STATIC FUNCTIONS
 ******************************************************************************/

/* Start impedance measurement using current profile */
void measurement_start(struct k_work * work)
{
    LOG_INF("%s", "Start measurement thread");
    m_app_state = APP_STATE_MEASURING;
    MEAS_Enable(true);
    k_thread_resume(measurement_thread_tid);
}

/* Stop immediateley any measurement in progress */
void measurement_stop(struct k_work * work)
{
    LOG_INF("%s", "Abort measurement thread");
	k_thread_suspend(measurement_thread_tid);
    MEAS_Enable(false);
}

static int32_t get_state_of_charge(const struct device *dev) {
    int status = 0;
    struct sensor_value state_of_charge, avg_current, voltage;

    status = sensor_sample_fetch_chan(dev, SENSOR_CHAN_GAUGE_STATE_OF_CHARGE);
    if (status < 0) {
        LOG_ERR("Unable to fetch state of charge");
        return -1;
    }

    status = sensor_channel_get(dev, SENSOR_CHAN_GAUGE_STATE_OF_CHARGE, &state_of_charge);
    if (status < 0) {
        LOG_ERR("Unable to get state of charge");
        return -1;
    }
    
    status = sensor_sample_fetch_chan(dev, SENSOR_CHAN_GAUGE_AVG_CURRENT);
    if (status < 0) {
        LOG_ERR("Unable to fetch avg current");
        return -1;
    }

    status = sensor_channel_get(dev, SENSOR_CHAN_GAUGE_AVG_CURRENT, &avg_current);
    if (status < 0) {
        LOG_ERR("Unable to get avg current");
        return -1;
    }
    
    status = sensor_sample_fetch_chan(dev, SENSOR_CHAN_GAUGE_VOLTAGE);
    if (status < 0) {
        LOG_ERR("Unable to fetch voltage");
        return -1;
    }

    status = sensor_channel_get(dev, SENSOR_CHAN_GAUGE_VOLTAGE, &voltage);
    if (status < 0) {
        LOG_ERR("Unable to get voltage");
        return -1;
    }

    LOG_INF("State of charge: %d%%, current: %d mA, voltage: %d mV", state_of_charge.val1, avg_current.val1 * 1000 + avg_current.val2 / 1000, voltage.val1 * 1000 + voltage.val2 / 1000);

    return state_of_charge.val1;
}

/* Bluetooth events callback */
void ble_evt_callback(ble_event_type_t event)
{
    switch(event)
    {
        case BLE_EVT_CONNECTED:
            k_work_submit(&start_measure);
            rgb_led_set(false, false, true);
            LOG_INF("BLE connected");
            break;
        case BLE_EVT_DISCONNECTED:
            k_work_submit(&stop_measure);
            rgb_led_blink_blue();
            LOG_INF("BLE disconnected");
            break;
        case BLE_EVT_NUS_ENABLED:
            rgb_led_set(false, true, false);
            LOG_INF("BLE NUS notifications enabled");
            break;
        case BLE_EVT_NUS_DISABLED:
            rgb_led_set(false, false, true);
            LOG_INF("BLE NUS notifications disabled");
            break;
    }
}

/* BLE NUS data received */
static void ble_rx_callback(const uint8_t *const p_data, uint16_t length)
{
    if (length > sizeof(message))
    {
        LOG_ERR("Size of message is %u but max is %u", length, Timestamp_size + 1);
        return;
    }
    memcpy(message, p_data, length);
    cobs_ret_t cobs_ret = cobs_decode_inplace(message, length);
    if (cobs_ret != COBS_RET_SUCCESS)
    {
        LOG_ERR("error %d while decoding cobs", cobs_ret);
        return;
    }

    /* Decode protobuf message (should be a request) */
    pb_istream_t istream = pb_istream_from_buffer(message + 1, length - 2);
    bool status = pb_decode(&istream, Timestamp_fields, &timestamp);
    if (!status) {
        LOG_ERR("protobuf decoding failed: %s\n", PB_GET_ERROR(&istream));
        return;
    }

    CAL_SetTime(timestamp.time, timestamp.us);
}

/* Init RGB gpios */
static void rgb_led_init(void)
{
    gpio_pin_configure_dt(&led_red_pin,   GPIO_OUTPUT_INACTIVE);
    gpio_pin_configure_dt(&led_green_pin, GPIO_OUTPUT_INACTIVE);
    gpio_pin_configure_dt(&led_blue_pin,  GPIO_OUTPUT_INACTIVE);
}

/* Set RGB state */
static void rgb_led_set(bool red, bool green , bool blue)
{
    /* if led was blinking we need to be sure that timer is stopped */
    k_timer_stop(&rgb_led_timer);
    gpio_pin_set_dt(&led_red_pin,   red);
    gpio_pin_set_dt(&led_green_pin, green);
    gpio_pin_set_dt(&led_blue_pin,  blue);
}

/* Start the RGB led blinking timer */
static void rgb_led_blink_blue(void)
{
    rgb_led_set(false, false, true);
    k_timer_start(&rgb_led_timer, K_MSEC(RGB_LED_BLINK_PERIOD), K_MSEC(RGB_LED_BLINK_PERIOD));
}

/* RGB led blinking timer callback */
static void rgb_led_timer_handler(struct k_timer *timer)
{
    gpio_pin_toggle_dt(&led_blue_pin);
}

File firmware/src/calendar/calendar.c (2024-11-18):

/**
 *******************************************************************************
 * @file    calendar.c
 * @author  Bertrand Massot (bertrand.massot@insa-lyon.fr)
 * @date    2022-02-24
 * @brief   Calendar module source file
 *******************************************************************************
 */

/*******************************************************************************
 * INCLUDES
 ******************************************************************************/

/* C Standard Library includes */
#include <stdint.h>
#include <time.h>

/* Zephyr Projet includes */
#include <zephyr/kernel.h>
#include <zephyr/device.h>
#include <zephyr/logging/log.h>
#include <zephyr/drivers/counter.h>

/* Application includes */
#include "calendar.h"

/*******************************************************************************
 * EXTERN VARIABLES
 ******************************************************************************/

/*******************************************************************************
 * PRIVATE MACROS AND DEFINES
 ******************************************************************************/
#define LOG_MODULE_NAME calendar
LOG_MODULE_REGISTER(LOG_MODULE_NAME);

#define TIMER DT_LABEL(DT_NODELABEL(rtc2))

#define ALARM_CHANNEL_ID (0)

#define RTC_PRESCALER (15)                                /**< Power of 2 for RTC frequency (15 is 32768 Hz) - TO BE SET ACCORDING TO PRESCALER IN DTS FILE */
#define RTC_FREQUENCY (1 << RTC_PRESCALER)                /**< RTC counter frequency in Hz (8 - 32768) */
#define COUNTER_TO_SECS(counts) (counts >> RTC_PRESCALER) /**< Macro to convert RTC counter value in seconds */
#define SECS_TO_COUNTER(secs) (secs << RTC_PRESCALER)     /**< Macro to convert seconds in RTC counter value */

/*******************************************************************************
 * PRIVATE TYPEDEFS
 ******************************************************************************/

/*******************************************************************************
 * STATIC VARIABLES
 ******************************************************************************/

static const struct device *counter_dev = DEVICE_DT_GET(DT_NODELABEL(rtc2));
static struct counter_top_cfg top_cfg;
static struct counter_config_info config_info;

static uint64_t time_offset = 0; /**< UNIX 64 bit epoch in seconds - Current time is time_offset + (RTC counter value converted in seconds) */
static uint32_t tick_offset = 0; /**< Microsecs offset set at initial time */

/*******************************************************************************
 * GLOBAL VARIABLES
 ******************************************************************************/

/*******************************************************************************
 * STATIC FUNCTION PROTOTYPES
 ******************************************************************************/

/* RTC Hardware Abstraction Layer */

static void rtc_init(void);
static void rtc_deinit(void);
static void rtc_set_time(const uint64_t timestamp, const uint32_t us);
static void rtc_get_time(uint64_t * p_timestamp, uint32_t * p_us);

static void counter_top_value_cb(const struct device *dev, void *user_data);

/*******************************************************************************
 * GLOBAL FUNCTIONS
 ******************************************************************************/

/**
 * @brief Initialize the calendar
 */
void CAL_Init(void)
{
    rtc_init();
    rtc_set_time(0ULL, 0UL);
}

/**
 * @brief Release the calendar
 */
void CAL_Deinit(void)
{
    rtc_deinit();
}

/**
 * @brief Update calendar time with Unix timestamp
 * @param[in] timestamp containing a Unix epoch
 */
void CAL_SetTime(const uint64_t timestamp, const uint32_t us)
{
    rtc_set_time(timestamp, us);
    LOG_INF("Time set to %llu UTC", timestamp);
}

/**
 * @brief Return current calendar time with Unix timestamp
 * @param[out] timestamp a pointer provided to store the Unix epoch read
 */
void CAL_GetTime(uint64_t *p_timestamp, uint32_t *p_us)
{
    rtc_get_time(p_timestamp, p_us);
}

/*******************************************************************************
 * STATIC FUNCTIONS
 ******************************************************************************/

/* RTC Hardware Abstraction Layer */
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

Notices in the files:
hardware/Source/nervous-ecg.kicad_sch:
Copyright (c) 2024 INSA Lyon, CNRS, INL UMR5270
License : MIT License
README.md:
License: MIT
